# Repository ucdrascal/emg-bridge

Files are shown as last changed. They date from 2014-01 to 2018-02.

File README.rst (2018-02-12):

==========
emg-bridge
==========

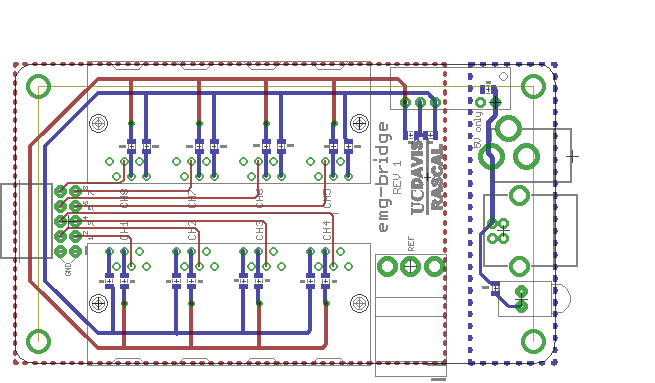
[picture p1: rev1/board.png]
Board screenshot


Description
===========

This board is for provding an interface between multiple Motion Labs Y03
amplifiers and a DAQ. The board provides RJ25 (6p6c modular jack) connectors
for plugging in up to 8 amplifiers. 5V power from either a barrel plug ("wall
wart") or USB-B is converted to +/-5V (isolated from power source, which
powers the amplifiers. The signal output from each amplifier is output through
a flat ribbon cable to the DAQ. A single ground electrode can be plugged in to 
a header pin.

License
=======

The contents of this repository are licensed under the `CC-BY 4.0 license`_.

.. REFERENCES
.. _`CC-BY 4.0 license`: https://creativecommons.org/licenses/by/4.0/

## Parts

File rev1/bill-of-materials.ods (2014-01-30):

manufacturer | part number | description | qty | unit price | vendor link
Recom Power | RKZ-0505D | 5V to +/-5V isolated DC converter | 1 | 8.72 | http://www.digikey.com/product-detail/en/RKZ-0505D/945-1200-ND/2256380
Molex Inc. | 670688000 | USB B connector | 1 | 1.36 | http://www.digikey.com/product-detail/en/0670688000/WM17113-ND/773801
CUI Inc. | PJ-002A | barrel power jack | 1 | 0.93 | http://www.digikey.com/product-detail/en/PJ-002A/CP-002A-ND/96962
Panasonic Electronic Components | ERJ-6GEYJ101V | 100 Ohm resistor | 16 | 0.10 | http://www.digikey.com/product-detail/en/ERJ-6GEYJ101V/P100ACT-ND/21875
Panasonic Electronic Components | ERJ-6GEYJ102V | 1k Ohm resistor | 1 | 0.10 | http://www.digikey.com/product-detail/en/ERJ-6GEYJ102V/P1.0KACT-ND/42833
Kemet | C0805C104K5RACTU | 0.1uF ceramic capacitor | 3 | 0.10 | http://www.digikey.com/product-detail/en/C0805C104K5RACTU/399-1170-1-ND/411445
Stewart Connector | SS-666604-NF | 4-position 6p6c modular jack | 2 | 5.15 | http://www.digikey.com/product-detail/en/SS-666604-NF/380-1032-ND/388294
TE Connectivity | 5-554710-3 | 6p6c modular plug | 8 | 0.44 | http://www.digikey.com/product-detail/en/5-554710-3/A9117-ND/255872
Assmann WSW Components | H1CXH-1036G | 2x5 header plug to flat cable assembly | 1 | 1.31 | http://www.digikey.com/product-detail/en/H1CXH-1036G/H1CXH-1036G-ND/999148
Sullins Connector Solutions | SBH11-PBPC-D05-RA-BK | 2x5 right angle shrouded header | 1 | 0.83 | http://www.digikey.com/product-detail/en/SBH11-PBPC-D05-RA-BK/S9177-ND/1990070
TE Connectivity | 640389-3 | 3x1 large header pins | 1 | 0.57 | http://www.digikey.com/product-detail/en/640389-3/A19920-ND/259207
Ligitek | LA93B/G-1 | green right angle LED in housing | 1 | 0.17 | http://www.jameco.com/webapp/wcs/stores/servlet/Product_10001_10001_104256_-1
 |  |  | total | 29.71

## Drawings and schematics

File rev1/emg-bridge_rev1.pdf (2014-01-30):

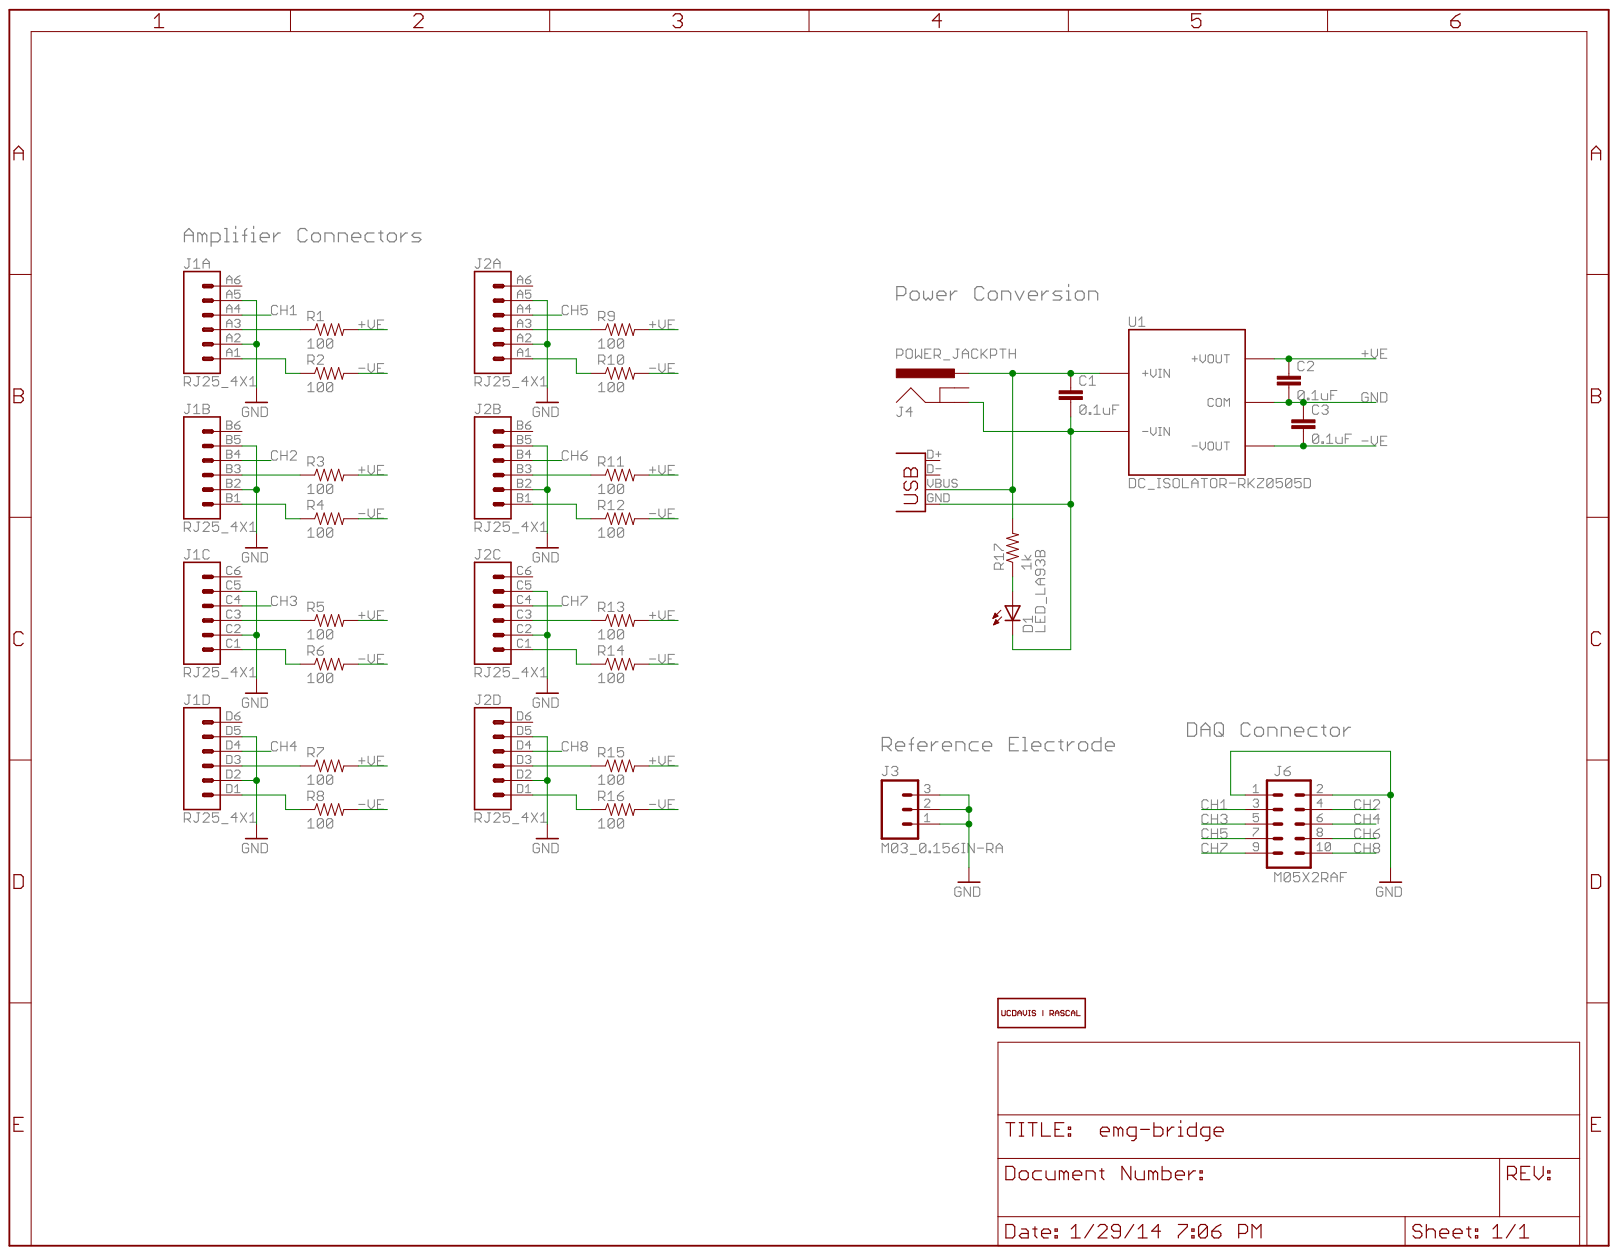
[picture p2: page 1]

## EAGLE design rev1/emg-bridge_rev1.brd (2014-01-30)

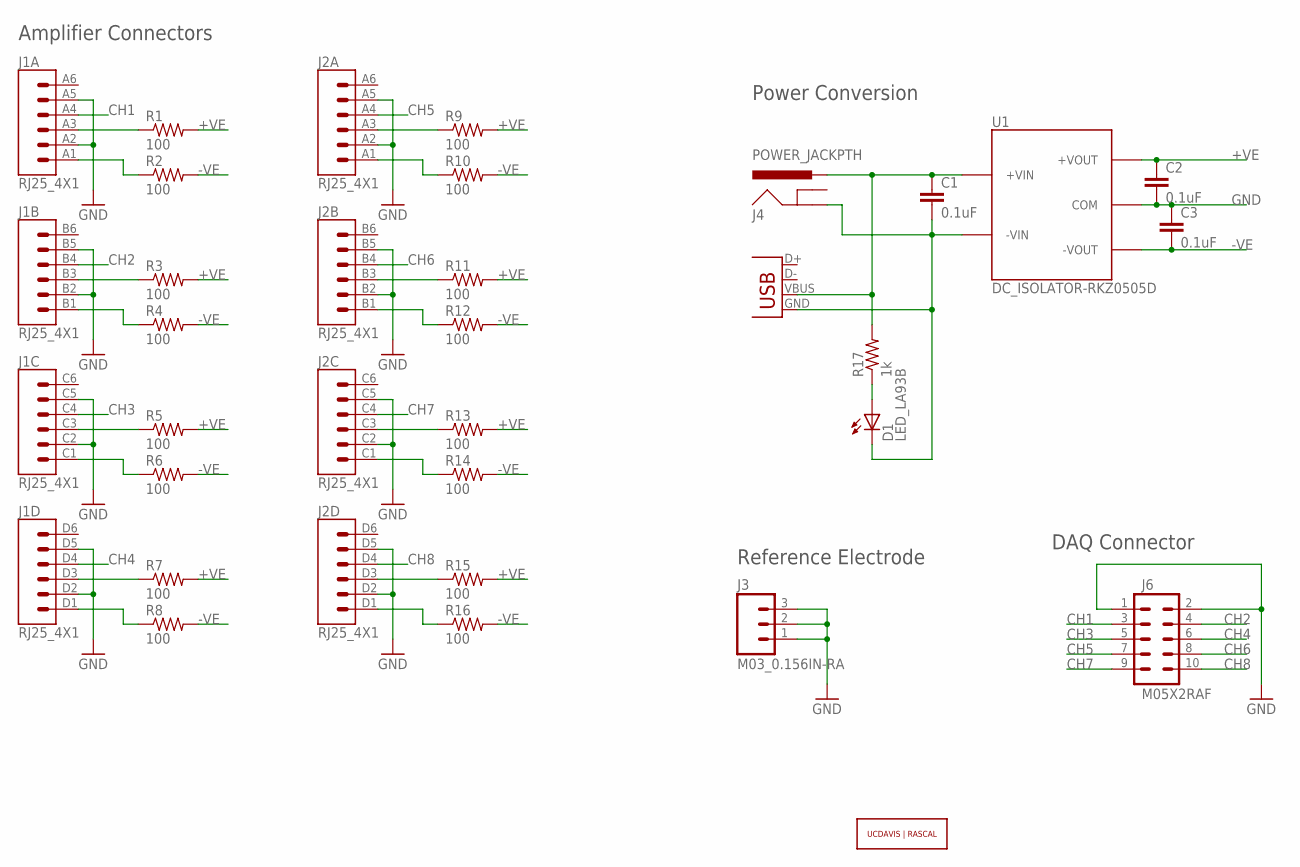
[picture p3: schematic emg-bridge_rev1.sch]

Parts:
C1, C2, C3: 0.1uF; 0805
D1: LED_LA93B; LED_RA
J1, J2: RJ25_4X1
J3: M03_0.156IN-RA; TE_640389-3
J4: POWER_JACKPTH; POWER_JACK_PTH
J5: USB-B; USB-B-PTH
J6: M05X2RAF; 2X5-RAF
R1, R2, R3, R4, R5, R6, R7, R8, R9, R10, R11, R12, R13, R14, R15, R16: 100; 0805
R17: 1k; 0805
U1: DC_ISOLATOR-RKZ0505D; SIP7
U$1: UCDAVIS-RASCAL_LOGO-2LINE; UCDAVIS-RASCAL_LOGO

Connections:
+VE: C2.1, R1.2, R3.2, R5.2, R7.2, R9.2, R11.2, R13.2, R15.2, U1.7 (+VOUT)
-VE: C3.2, R2.2, R4.2, R6.2, R8.2, R10.2, R12.2, R14.2, R16.2, U1.5 (-VOUT)
CH1: J1.A4, J6.3
CH2: J1.B4, J6.4
CH3: J1.C4, J6.5
CH4: J1.D4, J6.6
CH5: J2.A4, J6.7
CH6: J2.B4, J6.8
CH7: J2.C4, J6.9
CH8: J2.D4, J6.10
DGND: C1.2, D1.K (C), J4.GND, J5.GND, U1.2 (-VIN)
GND: C2.2, C3.1, J1.A2, J1.A5, J1.B2, J1.B5, J1.C2, J1.C5, J1.D2, J1.D5, J2.A2, J2.A5, J2.B2, J2.B5, J2.C2, J2.C5, J2.D2, J2.D5, J3.1, J3.2, J3.3, J6.1, J6.2, U1.6 (COM)
unnamed: J1.A1, R2.1
unnamed: C1.1, J4.PWR, J5.VBUS, R17.2, U1.1 (+VIN)
unnamed: J1.A3, R1.1
unnamed: D1.A, R17.1
unnamed: J1.B1, R4.1
unnamed: J1.B3, R3.1
unnamed: J1.C1, R6.1
unnamed: J1.C3, R5.1
unnamed: J1.D1, R8.1
unnamed: J1.D3, R7.1
unnamed: J2.A1, R10.1
unnamed: J2.A3, R9.1
unnamed: J2.B1, R12.1
unnamed: J2.B3, R11.1
unnamed: J2.C1, R14.1
unnamed: J2.C3, R13.1
unnamed: J2.D1, R16.1
unnamed: J2.D3, R15.1

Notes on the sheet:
Amplifier Connectors
Power Conversion
DAQ Connector
Reference Electrode

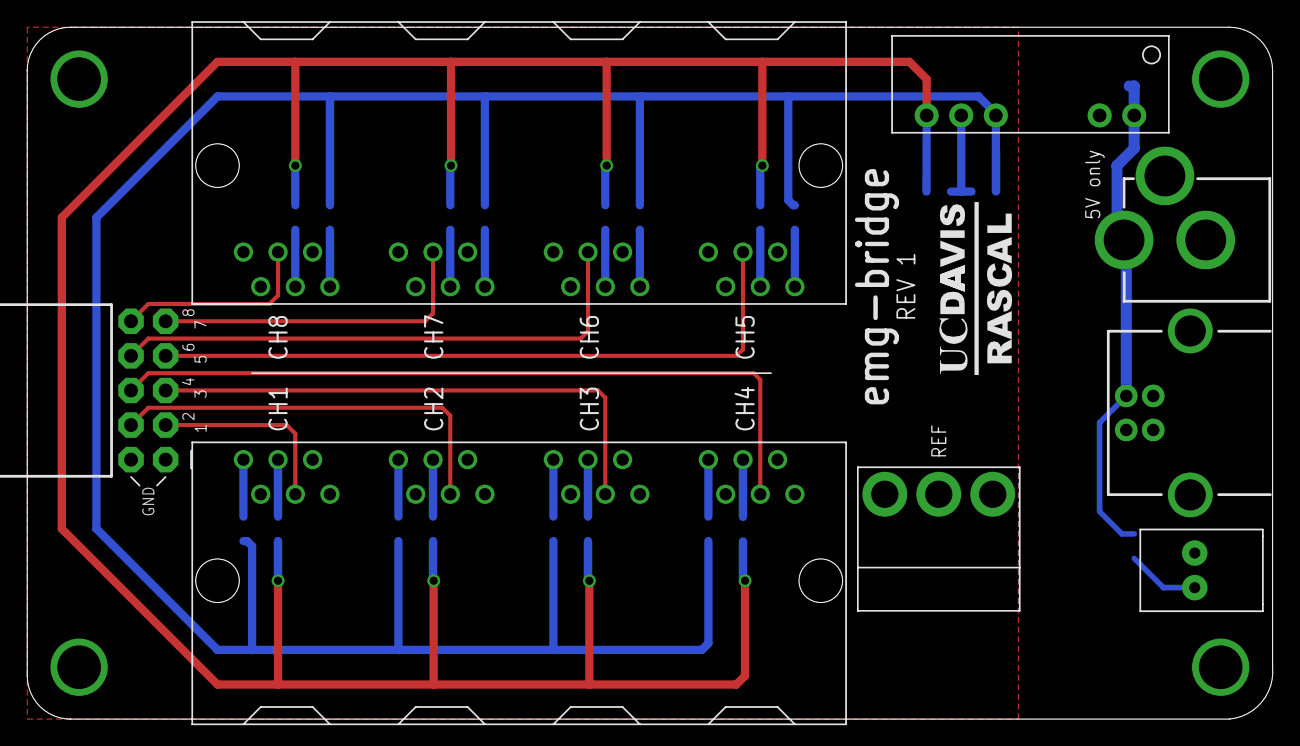
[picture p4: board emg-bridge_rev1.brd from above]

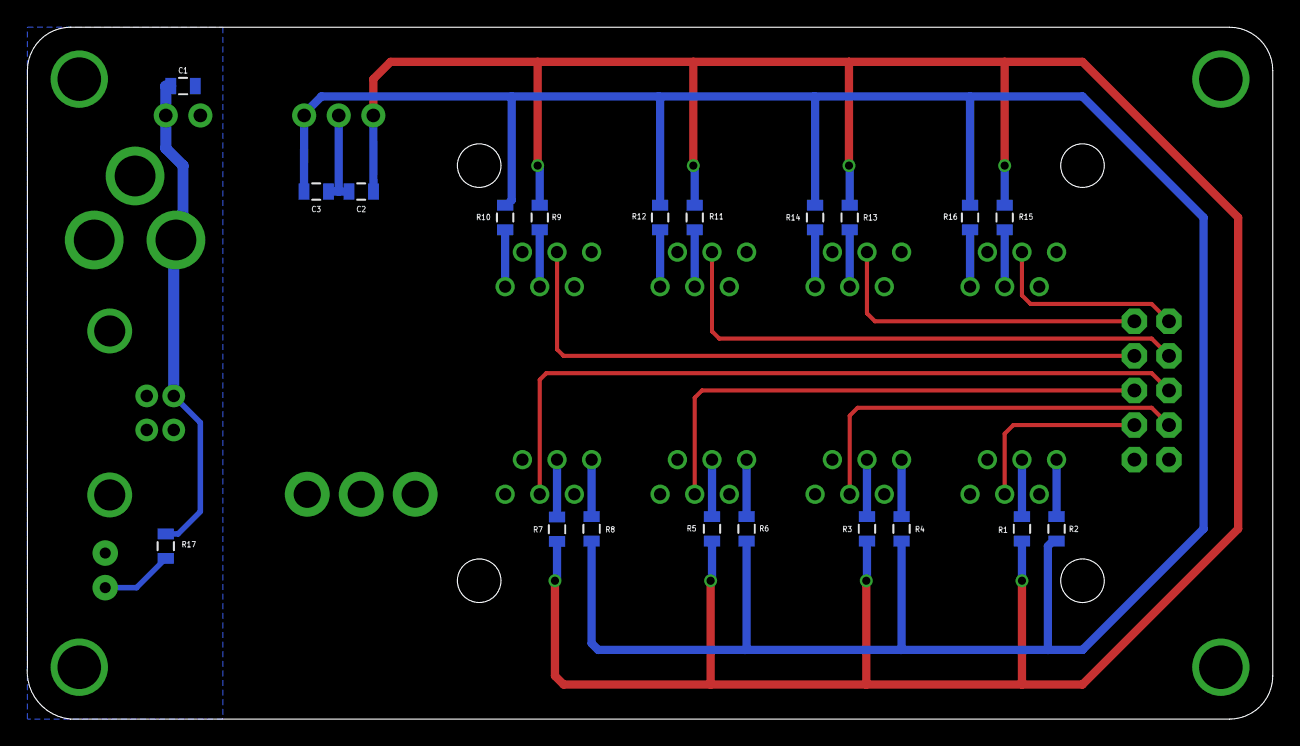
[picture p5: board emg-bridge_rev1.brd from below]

Board: 2 copper layers, 91.5 x 50.8 mm, 29 parts (20 on the bottom side), 30 nets.

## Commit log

2014-01-24 Initial commit.
    [bill-of-materials.ods, emg-bridge.brd, emg-bridge.sch]
2014-01-24 Added small note on the 2x5 header/connector to identify the red wire in the cable.
2014-01-25 Updated parts from eagle-lib. Worked out pinouts for all connectors.
    [emg-bridge.brd, emg-bridge.sch]
2014-01-27 Schematic cleaned up and board layout/routing rough draft completed.
    [emg-bridge.brd, emg-bridge.sch]
2014-01-27 Updated for eagle-lib changes. Finished up schematic.
    [emg-bridge.brd, emg-bridge.sch]
2014-01-28 Finished up layout and routing. Revision 1 complete.
    [emg-bridge.brd, emg-bridge.sch]
2014-01-28 Updated BOM.
    [bill-of-materials.ods]
2014-01-28 Added channel numbers on silkscreen.
    [emg-bridge.brd, emg-bridge.sch]
2014-01-29 Realization: the MC USB-1608G DAQ can only output 10mA for power, so the power circuitry has been completely reworked. Now with 3kV isolation!
    [bill-of-materials.ods, emg-bridge.brd, emg-bridge.sch]
2014-01-29 Added power jack.
    [emg-bridge.brd, emg-bridge.sch]
2014-01-29 Added power jack to BOM.
    [bill-of-materials.ods]
2014-01-29 Added LED.
    [bill-of-materials.ods, emg-bridge.brd, emg-bridge.sch]
2014-01-29 Changed a cap label to vector font.
    [emg-bridge.brd]
2014-01-30 Minor changes. Revision 1 should really be ready this time.
    [emg-bridge.brd, emg-bridge.sch]
2014-01-30 Revision 1 ordered and archived.
    [bill-of-materials.ods, emg-bridge_rev1.brd, emg-bridge_rev1.sch]
2018-02-12 Updated README
    - added screenshot of board layout
    - added LICENSE

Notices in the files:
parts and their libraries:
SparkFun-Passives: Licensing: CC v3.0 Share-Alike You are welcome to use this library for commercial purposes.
